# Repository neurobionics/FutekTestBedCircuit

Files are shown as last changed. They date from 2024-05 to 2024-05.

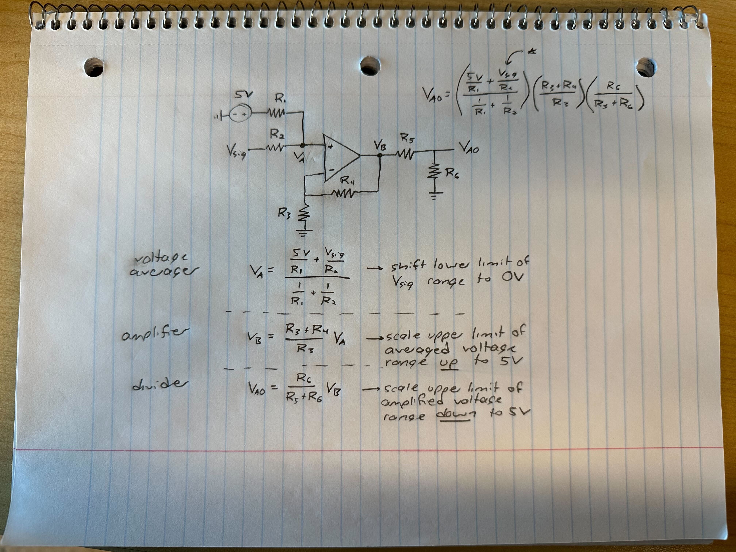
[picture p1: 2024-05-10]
IMG_1850.jpg

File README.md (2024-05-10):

# FutekTestBedCircuit

#This Circuit is used to connect the 0-5VDC output of the Futek Load Cell to an i2c message within the 0-3.3V range such that a Raspberry Pi can read it

Relevant People to talk to:

- Riley Peiper
- Megan Giacobetti

Relevant Resources to Use:

- Circuit Layout (see KiCAD Schema File and IMG) 
- The KiCAD Schematic (see KiCAD Schema File)
- The KiCAD PCB Design
- JLC PCB Account [For Ordering] - reach out to @Japmanjeet Singh Gill for login details 
- BOM and CPL Files (See FinalOrderingPackage Folder)

*Note- if cannot login to JLC PCB Account, see the image " JLCPCB COMPONENT PNs " and copy PNs from that file. Note - connectors J1, J2, J3 not placed in the production files. 
- J1 and J2 are through-hole placement and J3 has part shortages in china

To place J3 MOLEX Connector (Mouser PN: 538-203558-0607):
- Get the stencil in the lab
- Apply solder paste to the J3 Connector Area
- Place connector
- Use a hot air heat gun until the solder paste is melted!

To place J1 and J2 Through Hole Connectors (Mouse PN: 651-1984620) 
- Do regular through-hole placement with solder
- Be careful not to solder the pins to the ground layer on the front of the board

**Female Connector for the J3 Molex - Mouser PN: 538-501330-0600**

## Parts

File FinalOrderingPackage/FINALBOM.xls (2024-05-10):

Comment | Designator | Footprint | Quantity | NOTES | MANUFACTURING PN
10K | R4,R9,R2,R6,R1,R7,R15,R11,R17,R14,R18,R16,R10,R12,R8,R13 | R_0603_1608Metric | 16
0 | R3,R5 | R_0603_1608Metric | 2
ADS1115IDGS | U4 | VSSOP-10_3x3mm_P0.5mm | 1 |  | ADS1115IDGSR
L7805 | U3 | D2PAK-STB35NF10T4 | 1 |  | L7805ABD2T-TR
Conn_01x03 | J1,J2 | CONN_1984620_PXC | 2 | Do not place OR source this component - only drill the through holes
1u | C2,C3 | C_0603_1608Metric | 2
OP07 | U2,U1 | SOIC127P600X175-8N | 2 |  | OP07CSZ
Conn_01x06 | J3 | MOLEX_2035580607 | 1
FerriteBead | FB3,FB2 | BLM21AG102BH1J | 2 |  | BLM21SP601SH1D
0.1u | C1 | C_0603_1608Metric | 1
BSS138 | Q4,Q3,Q2,Q1 | SOT-23-3 | 4 |  | BSS138
0.33u | C4 | C_0603_1608Metric | 1

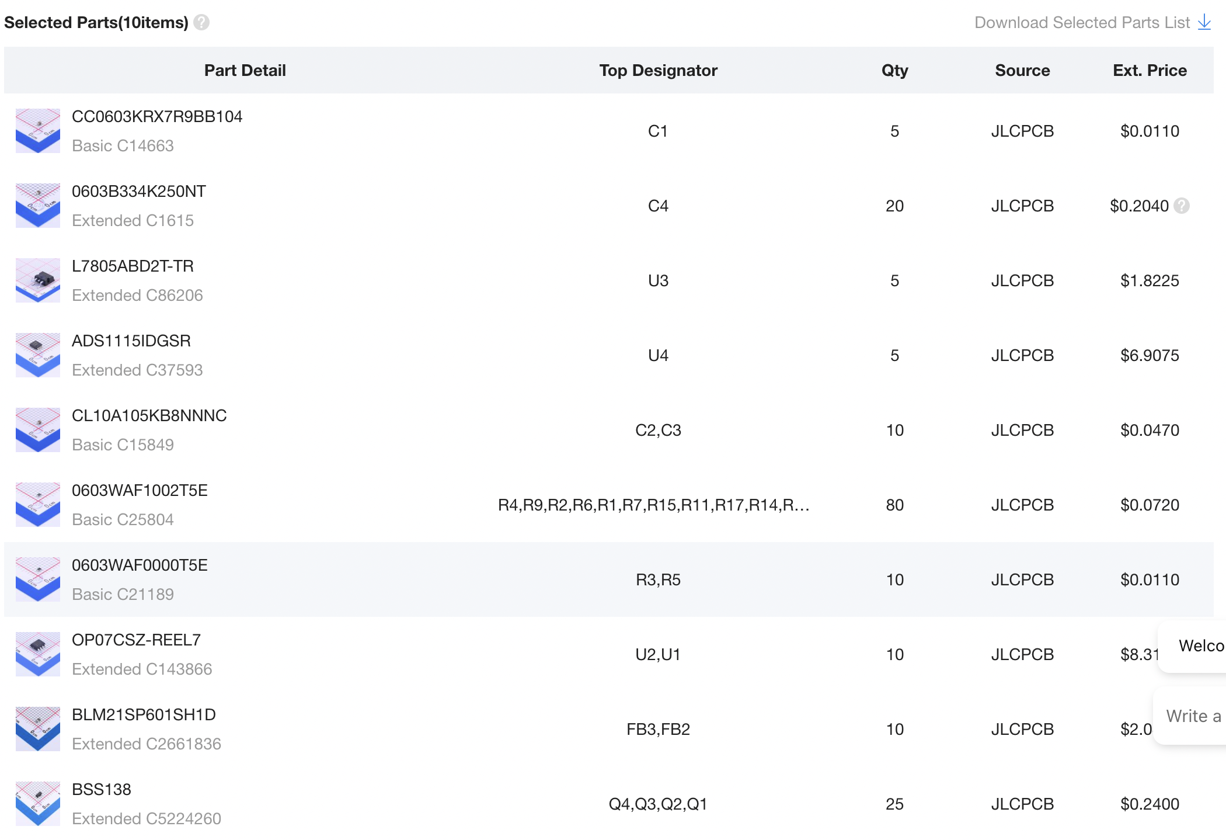
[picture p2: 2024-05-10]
JLCPCB COMPONENT PNs .png

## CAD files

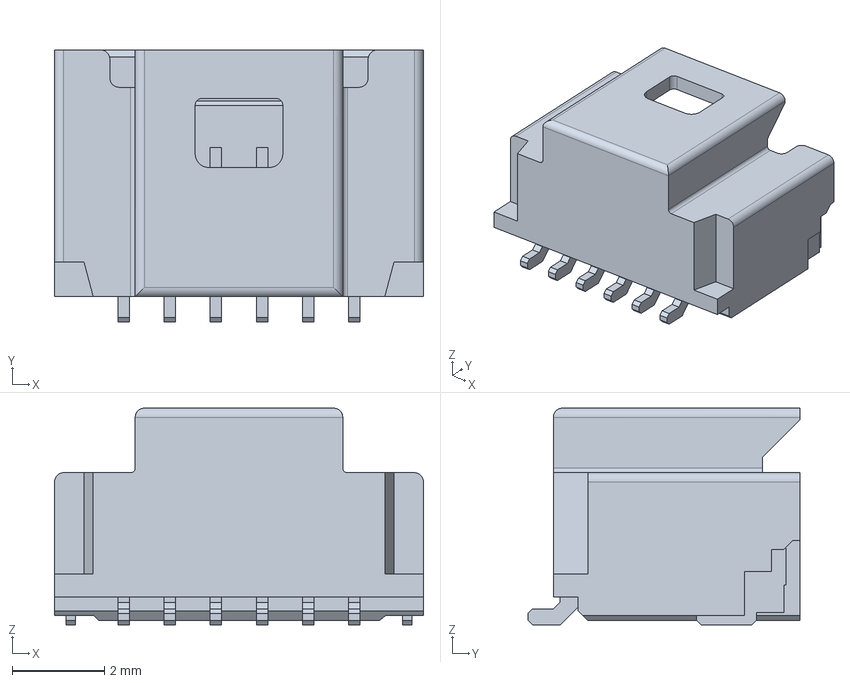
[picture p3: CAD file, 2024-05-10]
FutekCircuit_0213/Footprint Libraries/PicoClasp_MolexConnector2035580607/2035580607.step
8.00 x 5.90 x 4.70 mm

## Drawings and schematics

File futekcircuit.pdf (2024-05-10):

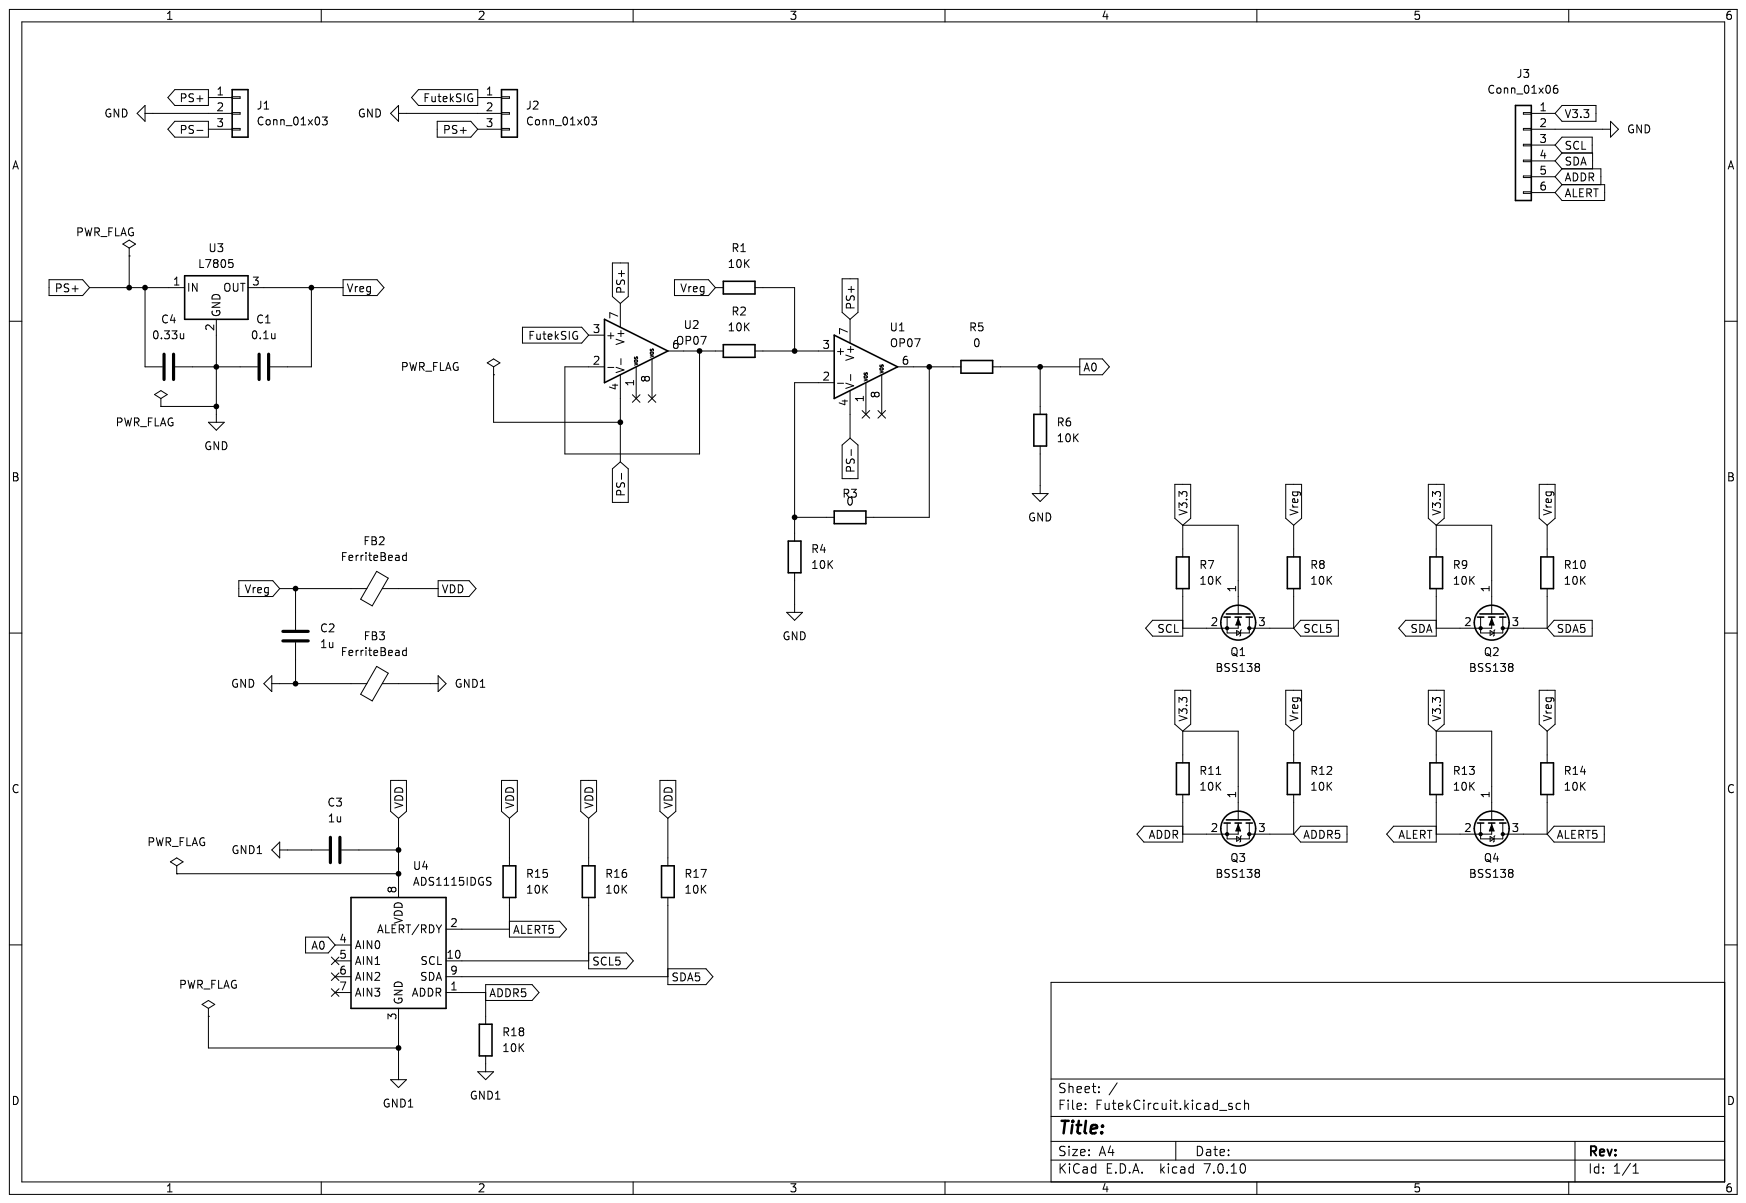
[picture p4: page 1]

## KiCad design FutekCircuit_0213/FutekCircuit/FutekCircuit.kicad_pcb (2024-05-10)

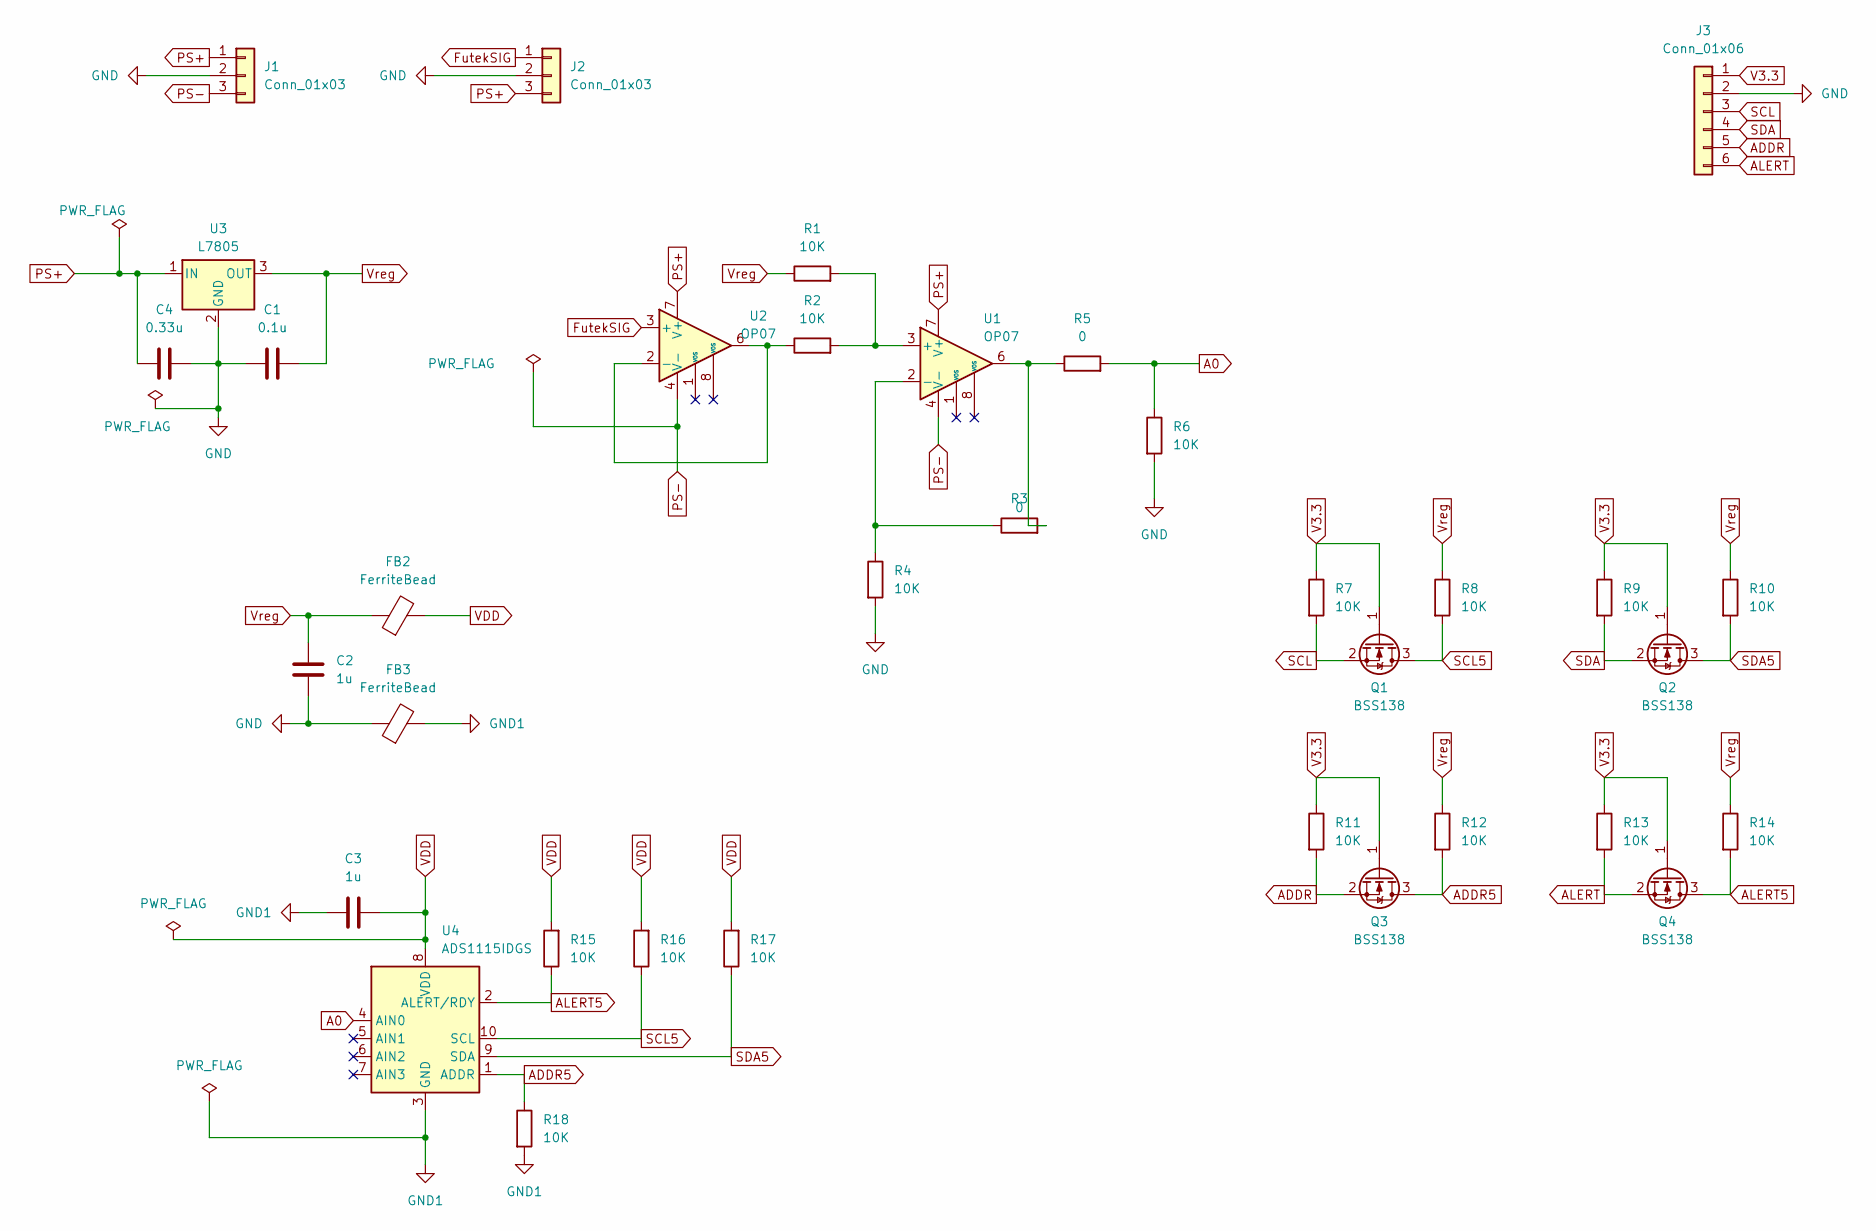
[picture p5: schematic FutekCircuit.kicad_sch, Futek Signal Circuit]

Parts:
C1: 0.1u; C_0603_1608Metric
C2, C3: 1u; C_0603_1608Metric
C4: 0.33u; C_0603_1608Metric
FB2, FB3: FerriteBead; BLM21AG102BH1J
J1, J2: Conn_01x03; CONN_1984620_PXC
J3: Conn_01x06; MOLEX_2035580607
Q1, Q2, Q3, Q4: BSS138; SOT-23-3
R1, R2, R4, R6, R7, R8, R9, R10, R11, R12, R13, R14, R15, R16, R17, R18: 10K; R_0603_1608Metric
R3, R5: 0; R_0603_1608Metric
U1, U2: OP07; SOIC127P600X175-8N
U3: L7805; D2PAK-STB35NF10T4
U4: ADS1115IDGS; VSSOP-10_3x3mm_P0.5mm

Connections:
A0: R5.2, R6.1, U4.4 (AIN0)
ADDR: J3.5, Q3.2 (S), R11.2
ADDR5: Q3.3 (D), R12.2, R18.1, U4.1 (ADDR)
ALERT: J3.6, Q4.2 (S), R13.2; also elsewhere on the board
ALERT5: Q4.3 (D), R14.2, R15.1, U4.2 (ALERT/RDY); also elsewhere on the board
FutekSIG: J2.1, U2.3 (+)
GND: C1.1, C2.2, C4.2, FB3.1, J1.2, J2.2, J3.2, R4.2, R6.2, U3.2 (GND)
GND1: C3.1, FB3.2, R18.2, U4.3 (GND)
unnamed: R3.2, R5.1, U1.6
unnamed: R1.2, R2.2, U1.3 (+)
unnamed: R3.1, R4.1, U1.2 (-)
unnamed: R2.1, U2.2 (-), U2.6
PS+: C4.1, J1.1, J2.3, U1.7 (V+), U2.7 (V+), U3.1 (IN)
PS-: J1.3, U1.4 (V-), U2.4 (V-)
SCL: J3.3, Q1.2 (S), R7.2
SCL5: Q1.3 (D), R8.2, R16.1, U4.10 (SCL)
SDA: J3.4, Q2.2 (S), R9.2
SDA5: Q2.3 (D), R10.2, R17.1, U4.9 (SDA)
V3.3: J3.1, Q1.1 (G), Q2.1 (G), Q3.1 (G), Q4.1 (G), R7.1, R9.1, R11.1, R13.1; also elsewhere on the board
VDD: C3.2, FB2.2, R15.2, R16.2, R17.2, U4.8 (VDD)
Vreg: C1.2, C2.1, FB2.1, R1.1, R8.1, R10.1, R12.1, R14.1, U3.3 (OUT)

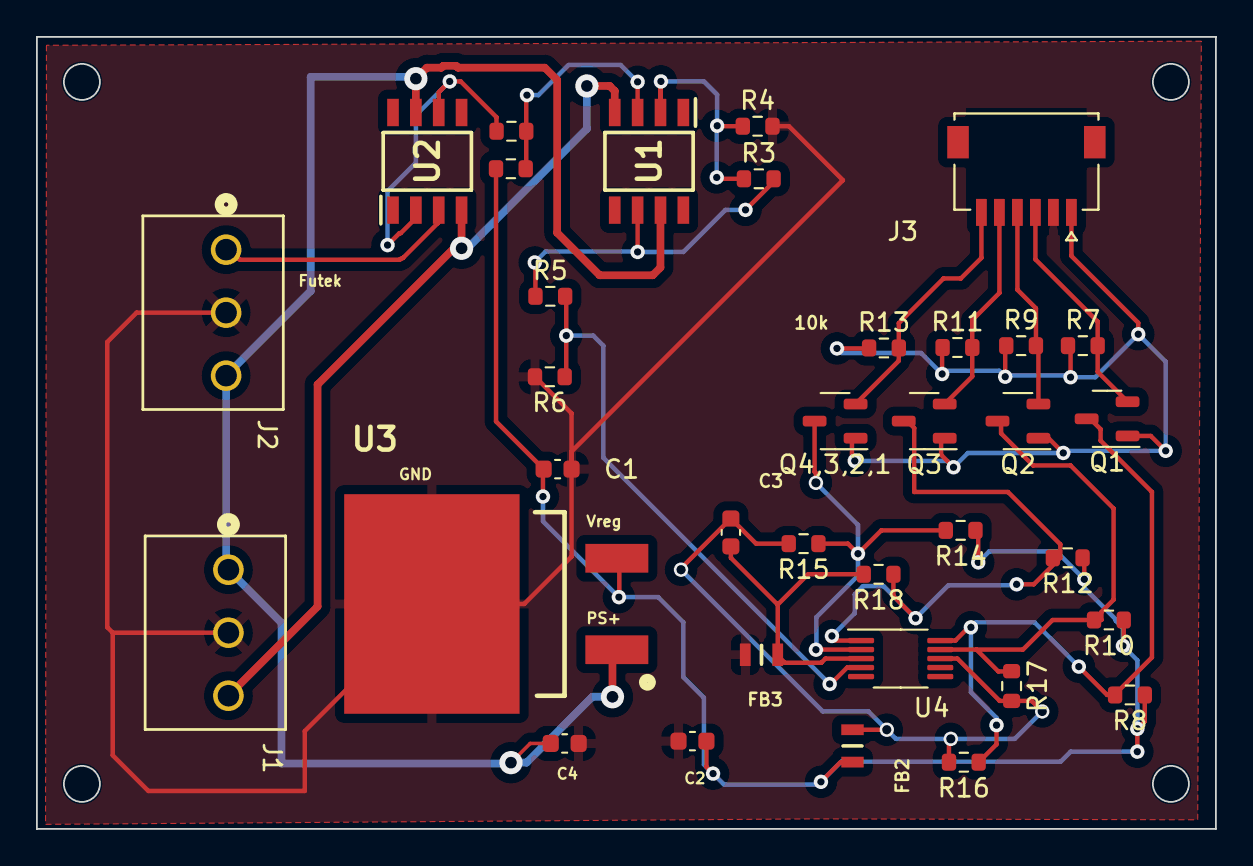
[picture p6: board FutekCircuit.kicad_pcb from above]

Board: 2 copper layers, 65.5 x 44.0 mm, 35 parts (0 on the bottom side), 21 nets.

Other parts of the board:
Q4,3,2,1: BSS138; SOT-23-3

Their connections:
ALERT: Q4,3,2,1.2 (S); also elsewhere on the board
ALERT5: Q4,3,2,1.3 (D); also elsewhere on the board
V3.3: Q4,3,2,1.1 (G); also elsewhere on the board

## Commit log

2024-05-10 KiCAD Circuit Files
    [2035580607.step, FutekCircuit.kicad_pcb, FutekCircuit.kicad_sch]
2024-05-10 Adding final files
    [FINALBOM.xls, FINALCPLfile.csv, FINALCPLfile.xls, FutekCircuit-B_Courtyard.gbr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]
2024-05-10 JLC PCB Component List

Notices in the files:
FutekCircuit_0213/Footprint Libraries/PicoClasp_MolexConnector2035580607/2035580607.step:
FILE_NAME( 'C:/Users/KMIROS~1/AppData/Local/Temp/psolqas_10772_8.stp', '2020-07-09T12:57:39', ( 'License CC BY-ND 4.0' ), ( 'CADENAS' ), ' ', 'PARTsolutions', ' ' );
